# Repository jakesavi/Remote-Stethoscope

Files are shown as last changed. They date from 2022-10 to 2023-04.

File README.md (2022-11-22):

# Remote-Stethoscope

## Communication
https://discord.gg/RNJMYp4RQn

## Data Pipeline 
- Heart
- Microphone
  - filter input frequency range
    - what frequency ranges are of interest?
    - do we want a discrete or analog UI for controlling inputs on the stethoscope?
  - amplify signal if analog mic
  - convert to digital signal if not a digital mic
  - potentially explore using multiple types of microphones and use input concensus to further filter out noise
- microcontroller processes raw input into audio format
- microcontroller streams unencrypted data to PC as a microphone
- PC software encrypts audio stream and sends to doctor in real-time
  - PC software on doctor's end decrypts audio stream and broadcasts to system audio output
- PC software (on user end or doctor's end?) saves an encrypted copy of the recording as an audio file (and sends it to doctor if on user's end)
  - Advantages of user's end file save:
    - Potential for packet loss of done on doctor's end
  - Advantages of doctor's end file save:
    - Doctor can segment the incoming real-time stream based on when the patient switches which body part is being listened to, allowing for an easier time with labeling the saved data for potential data visualization and AI applications

## Getting Started
1. Connect the Xiao RP2040 to your computer via USB-C cable
    - In order to boot the microcontroller into flashable mode, hold down the microcontroller push button labeled "B" from before the connection to the computer happens until after the LED on the microcontroller turns on.
2. To flash a new microcontroller with the software to act as a microphone, copy the file usb_microphone.uf2 into the root directory of the microcontroller.  It should automatically disconnect after this and reboot into a device that the system will refer to as MicNode
3. Connect the Xiao RP2040 to the MEMS digital microphone.  See "./doc/BreadboardCircuit.png" for a demonstration of of how the circuit should appear.
    - The microcontroller and microphone boards should both be soldered to their respective pin headers in order for this to work.
4. Open Audacity, select Microphone (MicNode) as your recording device, begin recording, and confirm that the microphone is recording a clear signal.
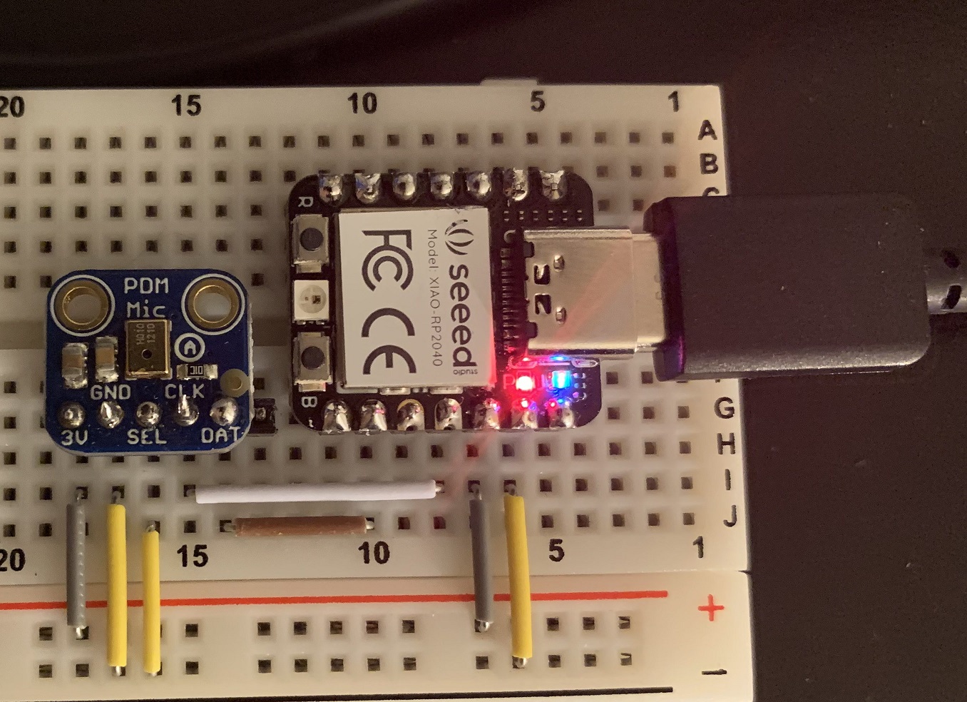
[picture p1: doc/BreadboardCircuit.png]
Circuit board connection map


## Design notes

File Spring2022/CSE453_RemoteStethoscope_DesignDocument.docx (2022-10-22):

# Design Document

# Remote Stethoscope

For use in Telemedicine

CSE 453 Hardware/Software Integrated System Design

Spring 2022

Andrew Burneson,

Yusuf Elazzazi,

Avi Tombak

# Table of Contents:

Project Background 3

Summary 3

Outcomes and Deliverables 3

Expected Timeline 3

Specifications 3

Requirements 3

Constraints 3

Design 3

Design Overview 3

Remote Stethoscope Block Diagram 4

Circuit Diagram 4

3D Printed Stethoscope Bell 5

Bill Of Materials 5

Prototyping 5

Testing/Verification 6

References Documentation 6

Project Delivery 6

# Project Background

Summary:

This project is a remote stethoscope device for use in telemedicine appointments. The remote stethoscope consists of a 3D printed stethoscope bell, a simple stethoscope diaphragm, a digital microphone, and a microcontroller. The remote stethoscope functions as a USB microphone device that can be used by patients during a telemedical appointment with a doctor. The remote stethoscope transmits audio of a patient’s heart, lung, and artery sounds for the doctor to listen to.

Client: Dr. Robert Gatewood

Outcomes/Deliverables: A Functional Prototype Remote Stethoscope

Expected Timeline: Delivered by end of the Spring 2022 semester

# Specifications

Requirements:

- The stethoscope will have a microphone to record audio input.
- The audio captured by the microphone will be amplified and converted to a digital signal.
- The digital audio will be transmitted to a computer using USB-C.
- The doctor will be able to receive the stethoscope audio over the internet.
- The stethoscope will come with a user manual for patients.

Constraints:

- The production cost of the stethoscope must be under $50.
- The microphone must record audio with a frequency between 20 and 2k Hz.
- The audio quality must be good enough for the doctor to diagnose the patient.

# Design

Design Overview:

The remote stethoscope was designed with simplicity and cost as its primary considerations. The stethoscope is to be used by patients directly, putting their health in their hands and allowing them to be more involved in their care. In its current design, the stethoscope acts very similarly to a traditional stethoscope. It must be pressed onto the chest to pick up a heartbeat or elsewhere for other bodily sounds. Instead of listening to the heartbeat via earpieces connected to the stethoscope, the remote stethoscope transmits audio of the heartbeat over USB C to a patient’s computing device. USB C was chosen as it is becoming widely used and available across multiple devices (PCs, smartphones, laptops, tablets). This model of the stethoscope consists of a 3D printed stethoscope bell, a plastic film diaphragm, a PDM MEMS microphone, and a microprocessor. The stethoscope has an overall production cost of $24.45.

Remote Stethoscope Block Diagram:

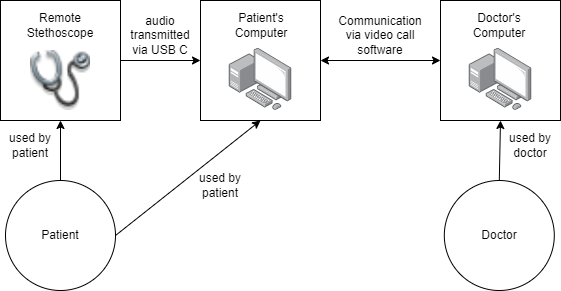
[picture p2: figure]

Circuit Diagram:

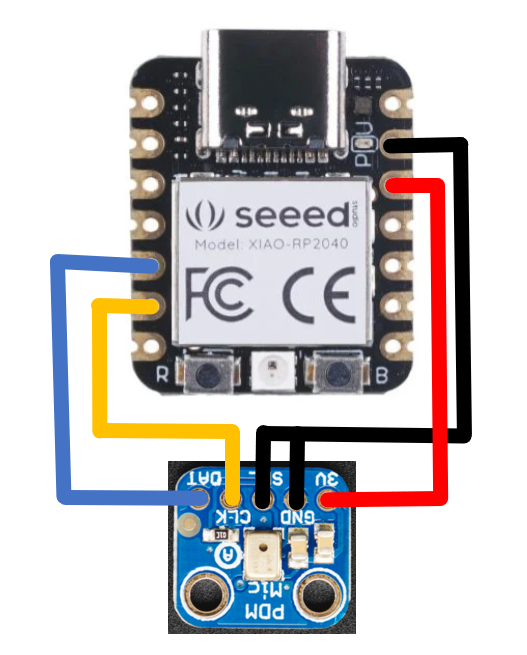
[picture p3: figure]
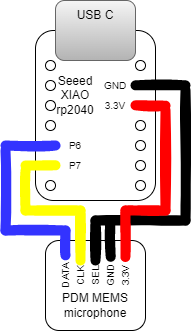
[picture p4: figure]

3D Printed Stethoscope Bell:

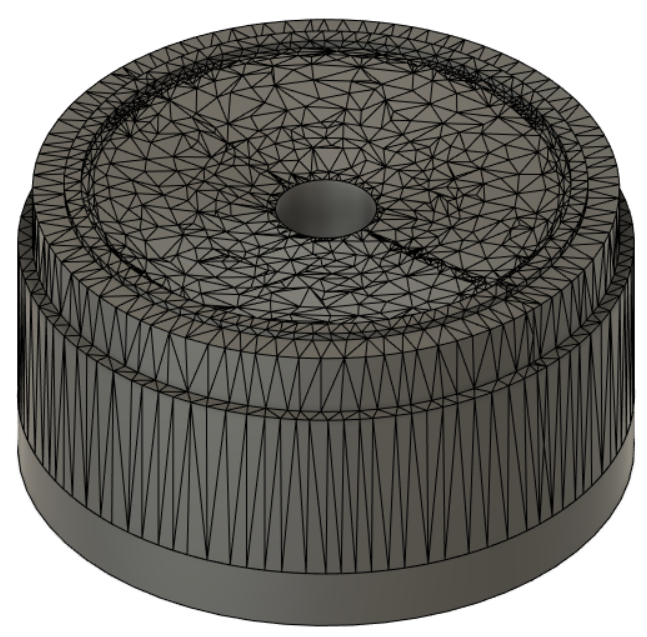
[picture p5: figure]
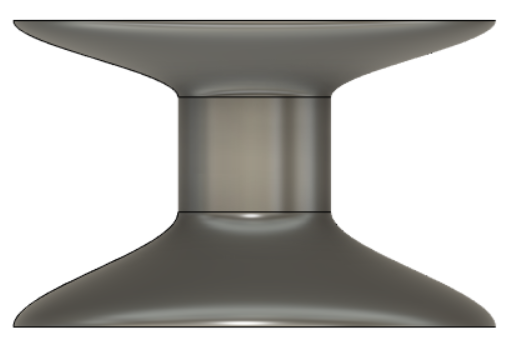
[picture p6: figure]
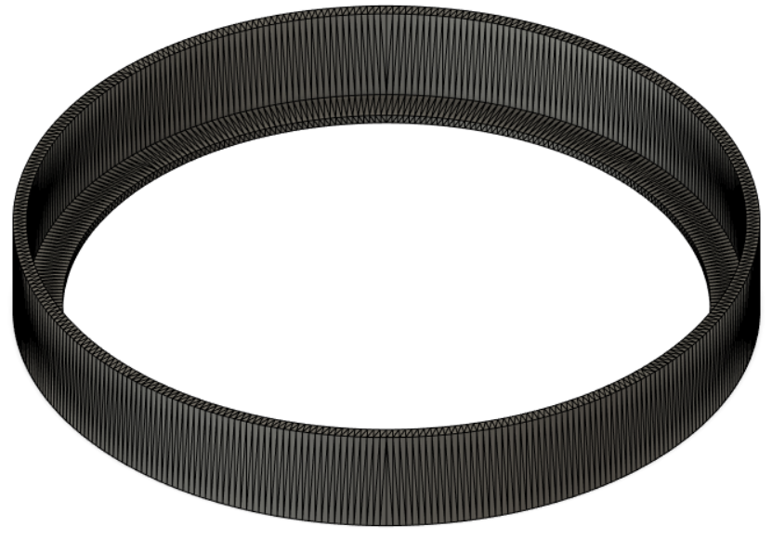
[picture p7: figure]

Stethoscope Head Stethoscope Handle Stethoscope Ring

Choice of Materials:

The following materials were chosen to ensure the stethoscope is well within the specified cost constraint.

- Seeed XIAO rp2040 Microcontroller for USB Microphone Device
- Adafruit PDM MEMS Microphone Breakout Board
- 3D Printed PLA Stethoscope Bell
- Report Cover Plastic Sheet for Stethoscope Diaphragm

Bill of Materials:

The bill of materials associated with this project is attached alongside this project and can also be found at: CSE453_RemoteStethoscope_BOM.docx (https://docs.google.com/document/d/1wtiuyCxSb0sfxCKr2Fo5E8p2Mzp0vhBN)

Prototyping:

This project has gone through many prototyping stages. There was an iterative design process for determining various factors of the design, including the stethoscope bell, the diaphragm, the microphone model, and the use of tubing. As this project was inherited from a previous group in this course, the prototyping first stated with testing and verification of their design. This involved circuit building and analysis. Moving on from the previous group’s work, a functional prototype utilizing a 3D printed stethoscope bell, and passing the audio recordings to a laptop via audio jack was created. This prototype does not reflect the final design but has sufficient audio quality for detecting heartbeats and other bodily sounds. After developing a working prototype with audiojack ( a far simpler protocol than usb audio) the next step was to develop the working USB microphone model. This was achieved using a Digital PDM MEMS Microphone and the Seeed XIAO rp2040 Microprocessor. The microprocessor was programmed using the ARM Developer Ecosystem Microphone Library for Pico. The stethoscope bell itself went through different iterations as well, first starting with an open source 3D printed stethoscope model found on thingiverse. A cone shaped stethoscope was also tested in prototyping. This design was modified to be larger and fit the stethoscope circuit. With this larger 3D printed stethoscope and microprocessor circuit, the final prototype design was produced.

Testing/Verification:

In order to test and verify the behavior of the stethoscope, audio recordings were taken from the USB device using the program Audacity. A heartbeat recording can be accessed here:

https://drive.google.com/file/d/168XsQzZ5z6yvc9MNJsx-UgUAekHpegst/view?usp=sharing

References Documentation:

The following references were used throughout the development of this project:

https://www.thingiverse.com/thing:2826304

https://github.com/ArmDeveloperEcosystem/microphone-library-for-pico

https://www.adafruit.com/product/3492?utm&gclid=CjwKCAjwyryUBhBSEiwAGN5OCKDwwzdIQs_0lFxj7LmzrSDqmjgVPmQrksxNdygoIFctDELNPU6doRoCHDYQAvD_BwE

https://www.seeedstudio.com/XIAO-RP2040-v1-0-p-5026.html?gclid=CjwKCAjwyryUBhBSEiwAGN5OCI7WuxWBaaORjbeqGIfqSfpMNfckhvS_kDpI4O9fUpDoT5V69NSQwBoCbkgQAvD_BwE

# Project Delivery

This Project will be ready for final delivery with a functional prototype, however our client is yet to schedule a date for delivery. The deliverables include our functional prototype remote stethoscope, and a user guide for patients.

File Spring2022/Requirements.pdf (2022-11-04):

# Remote Stethoscope Project Requirements Document

Prepared for: Dr. Robert Gatewood
Prepared by: Andrew Burneson, Yusuf Elazzazi, Avi Tombak, Quinn Tarbell

# Goals

The goal of this project is to develop an electronic stethoscope for use in remote medicine as well as an application to accompany it. To accomplish this, we will design, prototype, and test the stethoscope and program. The project will be completed by the first of April, 2022 with further refinement afterwards as necessary.

# Features

## Stethoscope

- Form Factor
- The stethoscope will have a head that attaches to a separate electronic component.
- The electronics will be inside a case small enough to fit in one hand.
- The stethoscope will have a cord that connects the electronics to a usb C port.
- The stethoscope head will have a microphone within it.
- The microphone will have a frequency range from 20 to 2k Hz.
- The microphone will have a high enough quality to be able to hear heart sounds.
- The electronics will include an amplification circuit.
- The electronics will include an analog to digital converter.

## Software

- The stethoscope will have one application designed to be used in conjunction with it.
- The application can create a host session.
- The user must input a password to start a host session.
- While hosting the user can accept requests to connect from other users.
- Once connected the host will receive audio from the other user’s application. ■ The host can listen to the received audio.
■ The host can adjust the volume of the received audio.
■ The host can record the received audio.
- The application can connect to a host application using a password.

- While connected to a host, the application can receive audio from the electronic stethoscope.
- While receiving audio the application will send the audio to the host application
- The application will function on Windows 10.

# Users

The stethoscope and application will be used by doctors and patients conducting remote medicine. The doctors include cardiologists, general practitioners, and etc. The patients include people who are quarantined, people who have trouble moving, the elderly, and people who live too far away from the doctor.
The doctor only needs to use the application. First the doctor will start the application and create a host session. Second, the doctor will send the patient the password and accept their request to connect. Then, the doctor will direct the patient to use the stethoscope and listen to the audio from it. The doctor can adjust the volume or record the audio using the application. The patient uses both the stethoscope and the application. First the patient will start the application and connect the stethoscope to the computer. Then they will input the password given by the doctor into the application. The patient will use the stethoscope to listen to their body as directed by the doctor.

# Constraints and Dependencies

- The stethoscope must cost less than fifty dollars.
- The stethoscope and application must be HIPPA compliant.
- The user must have a computer.
- The computer must run Windows 10.
- The computer must have a usb C port.
- The computer must have an internet connection.
- The user must have a connection to the internet.
- The internet connection must be fast enough to transmit real time audio.
- The doctor and patient must have a method to communicate with each other.

Description:
A remote stethoscope is to be designed for use in telemedicine appointments.
The patient will receive the stethoscope alongside a kit with a user guide and all necessary components.
The stethoscope will be used by the patient directly with doctor guidance via a video call. There is also a software component that will allow the doctor to analyze the stethoscope readings remotely.

The following is a diagram of the process the remote stethoscope recording will undergo from patient to doctor.

Remote Stethoscope Specifications:
- A cost of less than $50
- Sufficient audio quality and frequency range for hearing sounds of body systems (heart, lungs, gi)
- Record the audio and transmit it between the patient and doctor via other computing devices (i.e. a personal computer and/or a smartphone)
- Sufficient audio amplification and volume control
- Sufficient background noise filtration to isolate the body system sounds

Remote Stethoscope Patient/User Kit:
- Includes the remote stethoscope
- Includes any necessary cables and connectors for the stethoscope to interface with computers
- Includes a user guide document which has instructions on how to use the stethoscope

Remote Stethoscope Software Interface:
- Allow for easy analysis of the stethoscope readings by the doctor
Goals:
The aim of this project is to continue the work done by the previous group in charge of the remote stethoscope project. The goal is to create a cheap electronic stethoscope as well as a system to transmit audio over the internet for use in telemedicine. The stethoscope must be cheap in order for it to be accessible to patients.

Users:

The remote stethoscope would be used by patients and doctors conducting telemedicine. The patients will be within their homes. The patients will run the application and connect the stethoscope to their computer with a cable. The doctor will also run the application and connect it to the patient’s application over the internet. The patient will then place the stethoscope on their body under the doctor's direction while the doctor listens to the audio using the application on their own computer.

Features:
The stethoscope will be able to detect sounds in the range of frequencies necessary for diagnosis. It will amplify the audio and have sufficient audio quality in order for the doctor to diagnose medical issues. The stethoscope will connect to a computer through a cable. The application will record the audio from the stethoscope and transmit it over the internet to the doctor’s computer. The application on the doctor’s computer will play the audio and allow them to control the volume.

Constraints:
The stethoscope must cost less than 50 dollars.

Requirements:
The patient and doctor must both have a computer and an internet connection.

# Outline

I. Goals
A. Develop Remote Stethoscope
1. Design
2. Prototype
3. Test
B. Develop Software
1. Design
2. Prototype
3. Test
C. Complete by Deadline (add deadline) II. Features
A. Remote Stethoscope
1. Form Factor
a) Has a stethoscope head
b) Has an electronic circuit
c) Head connects to circuit
d) Circuit in case small enough to fit in hand
2. Connector between circuit and computer (choose one connector)
3. Microphone in stethoscope head
a) (add frequency range)
b) High sound quality (not specific)
4. Amplification Circuit
a) Amplification factor (undecided)
b) Analog to Digital Converter (ADC)
(1) May be part of computer if using microphone jack
B. Software
1. Can create a host
a) Generates password
b) Can accept requests to connect from guests
c) Receives audio from guest
(1) Plays received audio
(2) Can adjust volume
(3) Can record audio
2. Guest
a) Can request to connect with a host using a password
b) Receives audio from stethoscope
c) Sends audio from stethoscope to host
3. Functions on OS (choose one operating system)
III. Users
A. Who uses it?
1. Doctors
a) Cardiologists

b) General Practitioners
c) (Ask Dr. Gatewood for more)
2. Patients
a) Quarantined
b) Trouble moving
c) Elderly
d) Live to far away
B. How is it used
1. Doctors
a) Launch application
b) Start hosting
c) Give patient password
d) Accept patient’s connection request
e) Instruct patient to use stethoscope
f) Listen to audio from stethoscope
g) Adjust volume
h) Record audio
2. Patient
a) Launch application
b) Connect stethoscope to computer
c) Input password given by doctor
d) Use stethoscope as directed by doctor IV. Constraints
A. Must cost less than $50
B. Must be HIPPA compliant
V. Dependencies
A. User must have a computer
1. The computer must have the correct OS
2. The computer must have the correct connection
3. The computer must be able to connect to the internet
B. The user must have an internet connection
1. The connection must be fast enough to transmit real time audio
C. The doctor and patient must be able to communicate

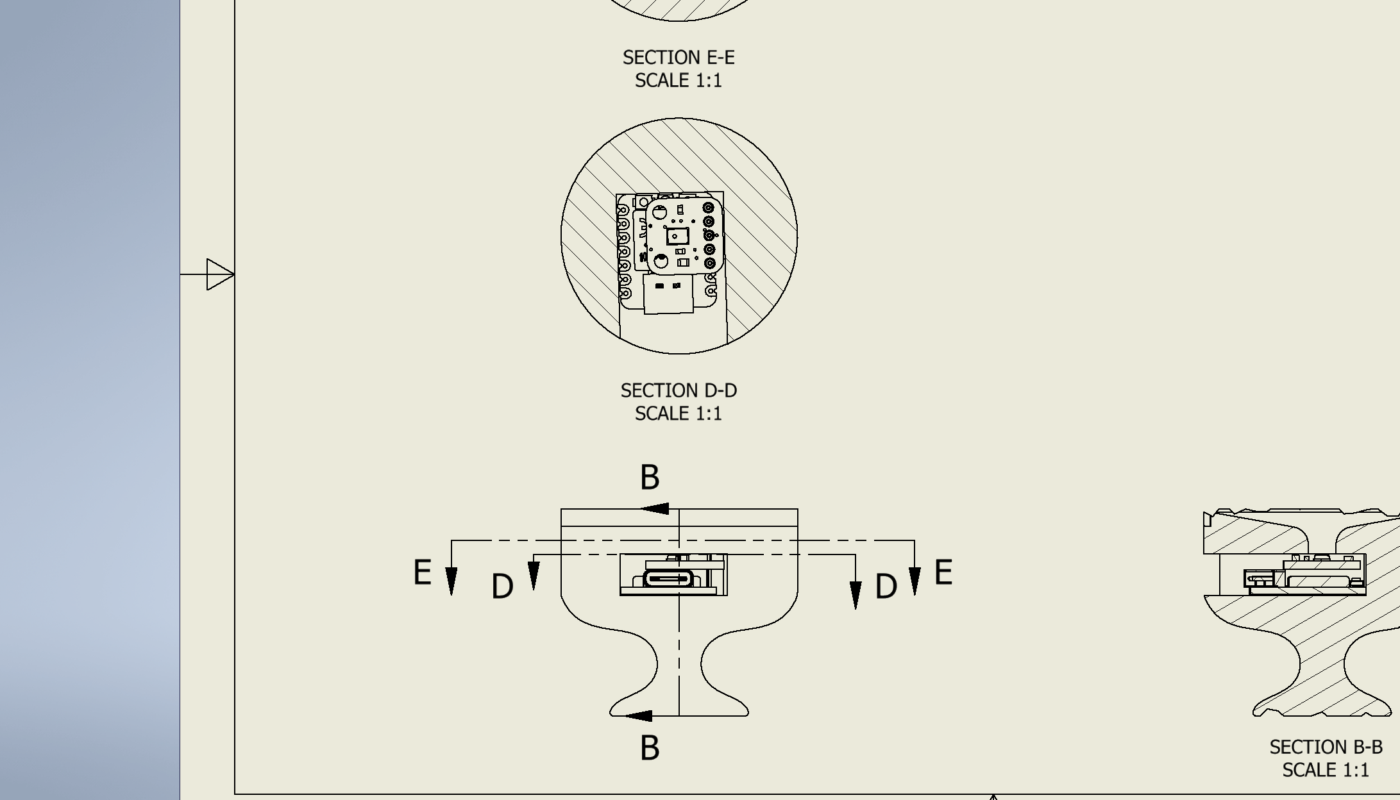
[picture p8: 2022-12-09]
3D_models/Fall2022_revision/Full_Stethoscope_Body.png

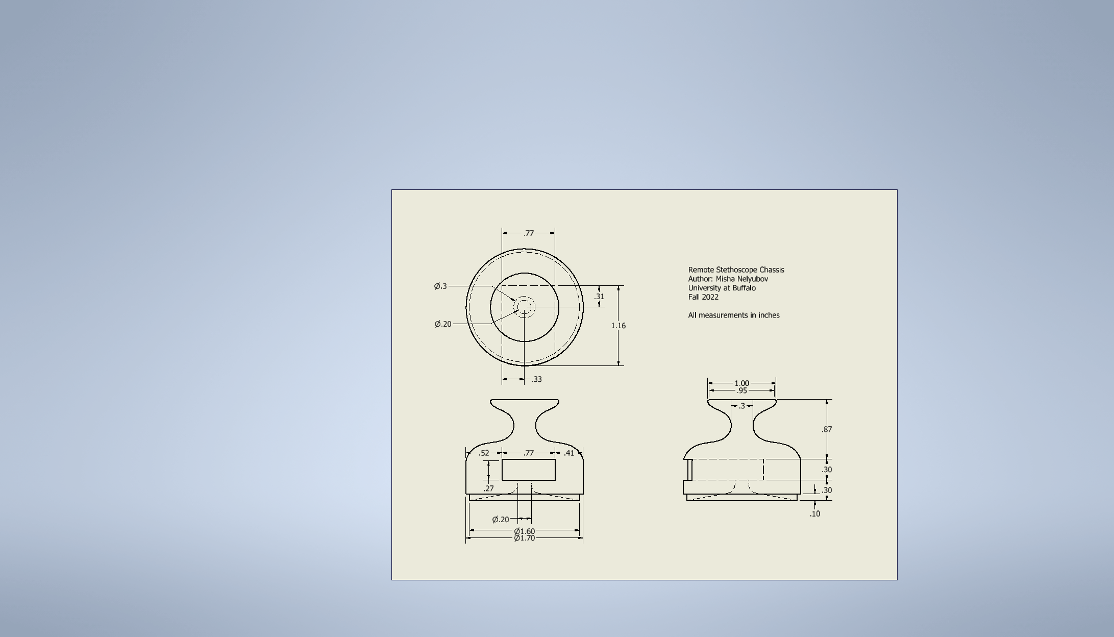
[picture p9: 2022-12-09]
3D_models/Fall2022_revision/Stacked_Case.png

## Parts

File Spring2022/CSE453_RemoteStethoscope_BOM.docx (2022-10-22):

Image | Part Name & Part Number | Supplier / Manufacturer | Part Type & Use | Quantity | Cost per Purchase | Cost per Stethoscope | Link | Associated Documentation

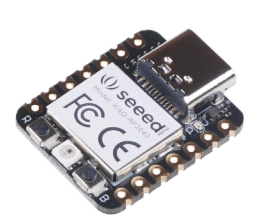
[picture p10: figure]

| XIAO rp2040 SKU: 102010428 | Seeed | Microcontroller for powering stethoscope and allowing it to be treated as a USB microphone | 1 board | $5.40 | $5.40 | seeed_XIAO_rp2040 (https://www.seeedstudio.com/XIAO-RP2040-v1-0-p-5026.html) | datasheet (https://files.seeedstudio.com/wiki/XIAO-RP2040/res/rp2040_datasheet.pdf)

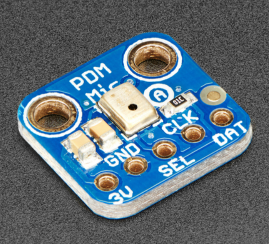
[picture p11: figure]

| PDM MEMS Microphone Breakout PRODUCT ID: 3492 | Adafruit | Microphone for stethoscope functionality | 1 board | $4.95 | $4.95 | PDM_MEMS_mic (https://www.adafruit.com/product/3492?utm) | mic_documentation (https://cdn-learn.adafruit.com/downloads/pdf/adafruit-pdm-microphone-breakout.pdf)

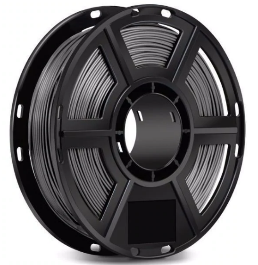
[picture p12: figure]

| PLA Filament for Finder, Dreamer, Inventor Series, & Adventurer 3 Part Number: N/A | FlashForge | 3D Printer Filament for stethoscope material | head: 130.7g handle: 63.87g ring: 7.47g total: 202.4g | $34 | ~ $13.76 | PLA_filament (https://flashforge-usa.com/collections/materials/products/pla-filament-for-finder-dreamer-and-inventor-models) | N/A

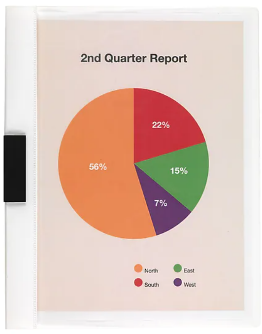
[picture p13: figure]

| Slide Locking Report Covers, Letter, White, 5/Pack Item #: 919872 Model #: 20592 | Staples | Plastic Sheet for stethoscope diapragm | 1 cutout (4 per sheet) | $6.79 | ~ $0.34 | diaphragm_material (https://www.staples.com/Staples-Side-Lock-Report-Covers-5-Pack-White-20592/product_919872) | N/A
| | | | | | Total cost: ~ $24.45

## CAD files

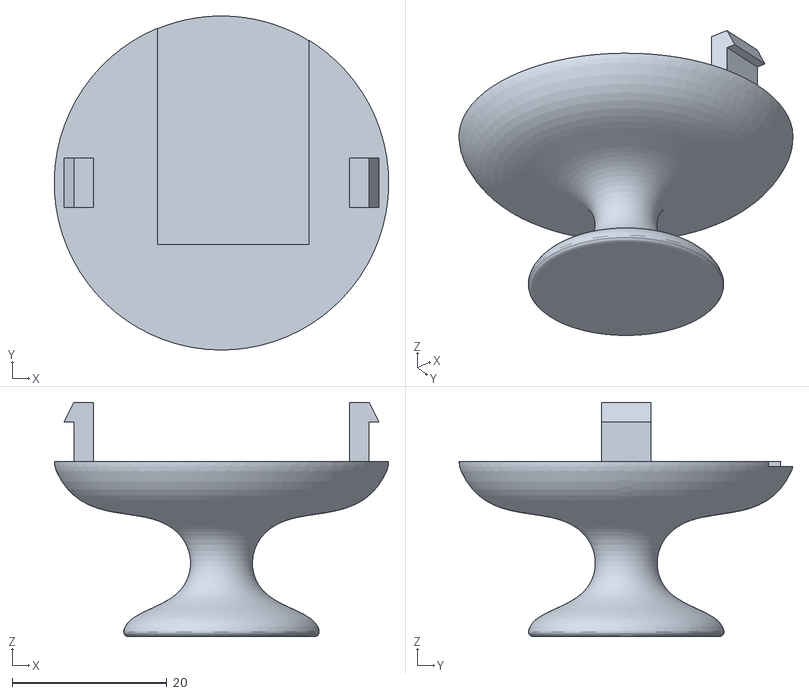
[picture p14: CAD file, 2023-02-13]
3D_models/Fall2022_revision/Stacked_Case_handle.stl
43.2 x 43.1 x 30.3

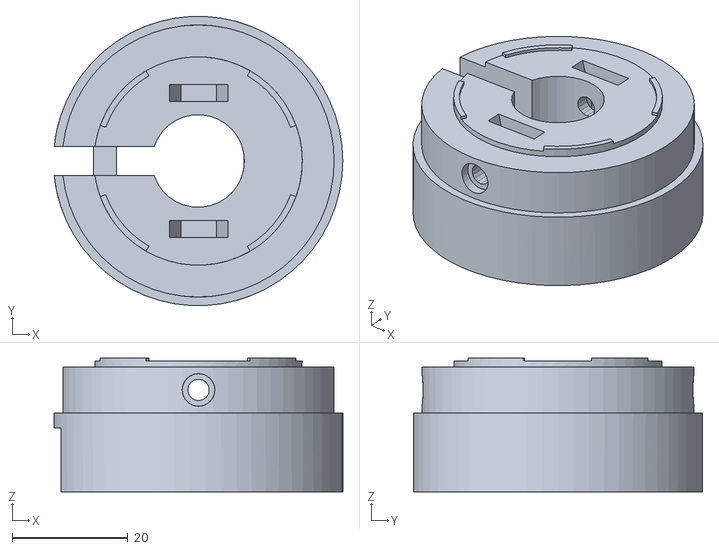
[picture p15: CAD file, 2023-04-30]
3D_models/ThonkLabs 1ne/STL files/PiezoMount.stl
49.9 x 49.9 x 23.1

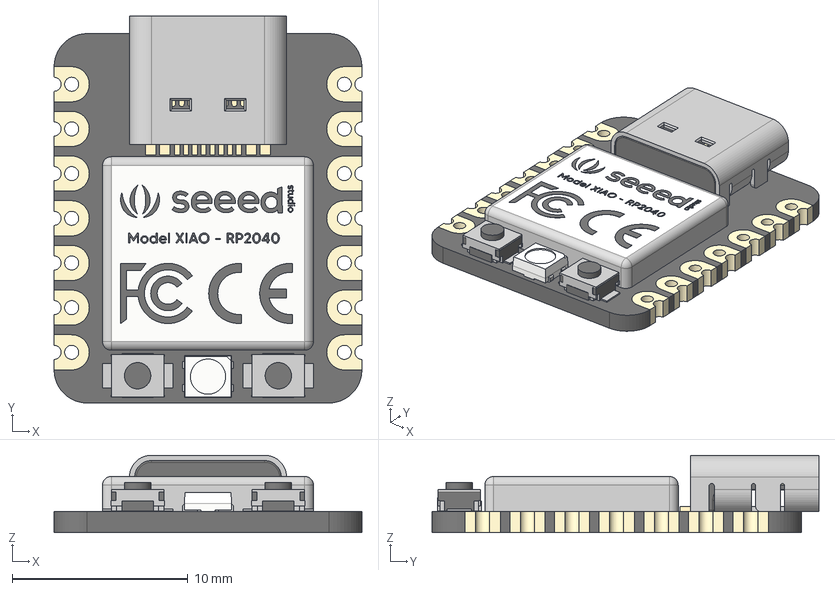
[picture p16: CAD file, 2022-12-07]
3D_models/xiao_rp2040/Seeed Studio XIAO RP2040 v26.step
17.5 x 22.0 x 4.40 mm
type-c v2
smd_button v3
DOUT
DIN
VSS
VDD
smd_button v3(Mirror)

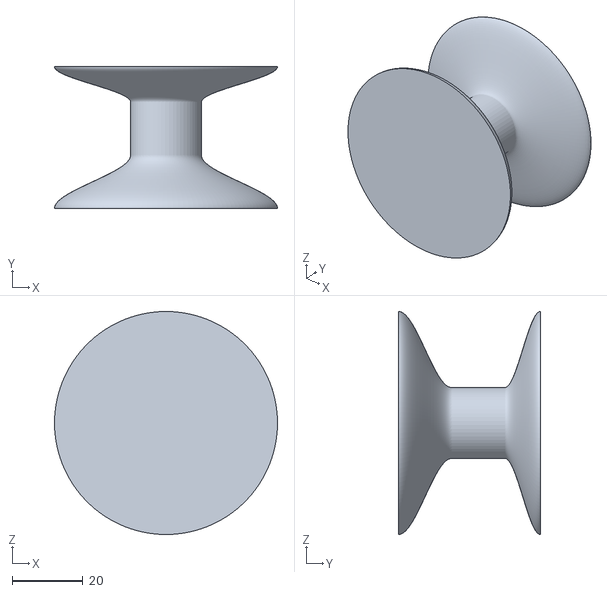
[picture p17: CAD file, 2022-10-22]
Spring2022/CSE453_RemoteStethoscope_3DPrints/handle.stl
63.0 x 40.0 x 63.0

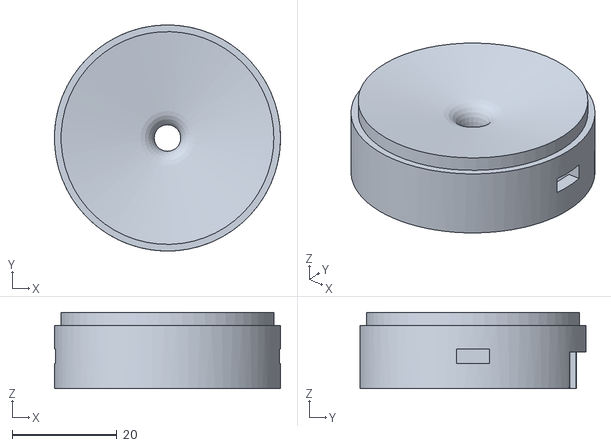
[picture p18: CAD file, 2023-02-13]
3D_models/Fall2022_revision/Stacked_Case_container.stl
43.2 x 43.2 x 14.6

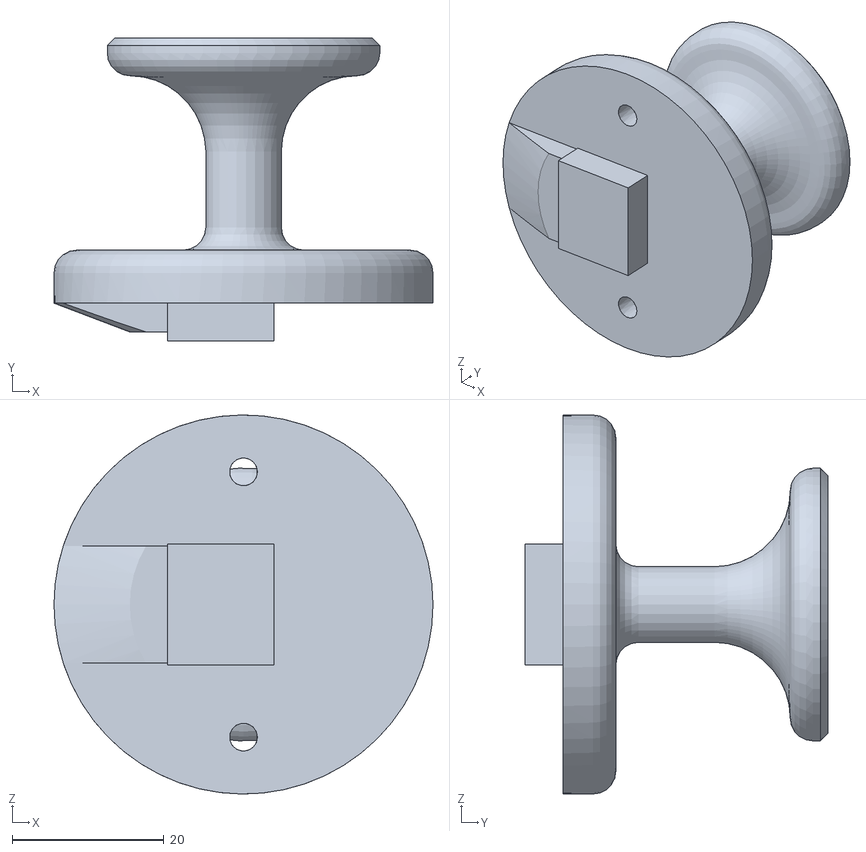
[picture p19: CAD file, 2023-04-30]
3D_models/ThonkLabs 1ne/STL files/holding_socket.stl
50.0 x 40.0 x 50.0

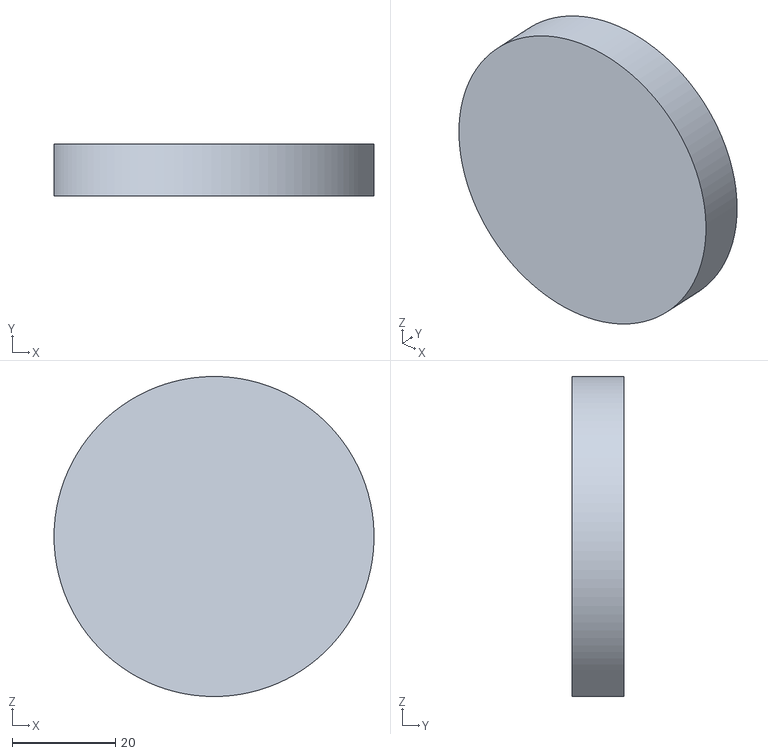
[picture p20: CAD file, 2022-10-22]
Spring2022/CSE453_RemoteStethoscope_3DPrints/diaphragm_stencil.stl
62.0 x 10.0 x 62.0

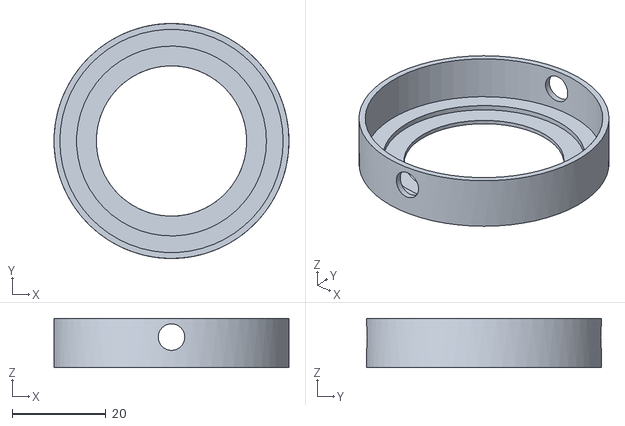
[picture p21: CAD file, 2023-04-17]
3D_models/ThonkLabs 1ne/STL files/Diaphragm_lock.stl
50.0 x 50.0 x 10.5

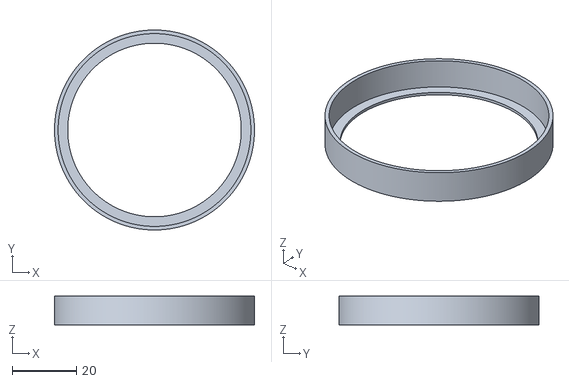
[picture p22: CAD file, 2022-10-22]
Spring2022/CSE453_RemoteStethoscope_3DPrints/ring.stl
62.2 x 62.2 x 9.00

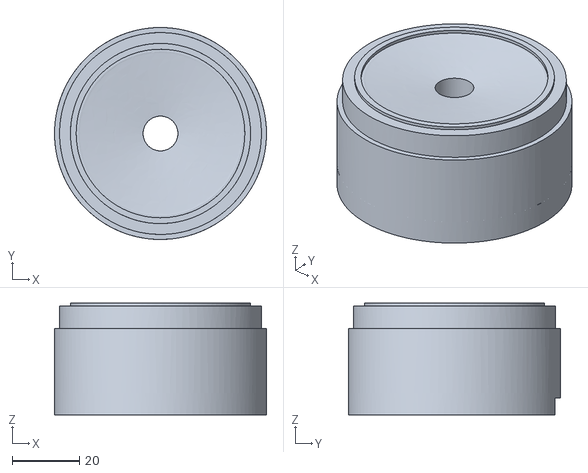
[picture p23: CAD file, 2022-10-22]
Spring2022/CSE453_RemoteStethoscope_3DPrints/head.stl
63.0 x 63.0 x 33.2

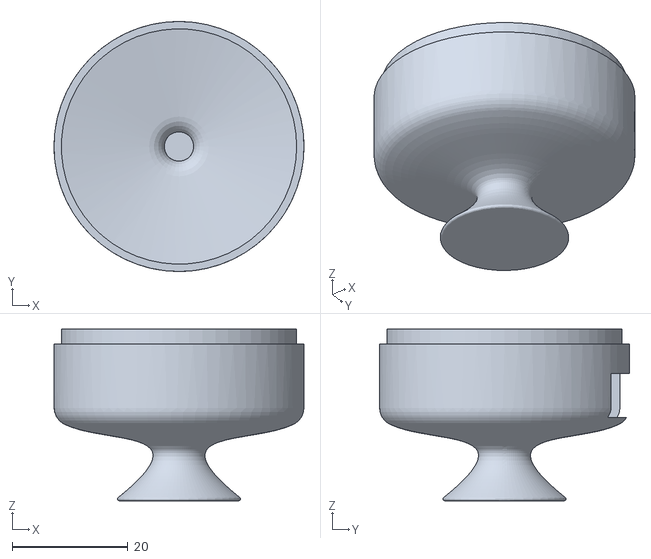
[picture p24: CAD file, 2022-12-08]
3D_models/Fall2022_revision/Stacked_Case.stl
43.2 x 43.2 x 29.6

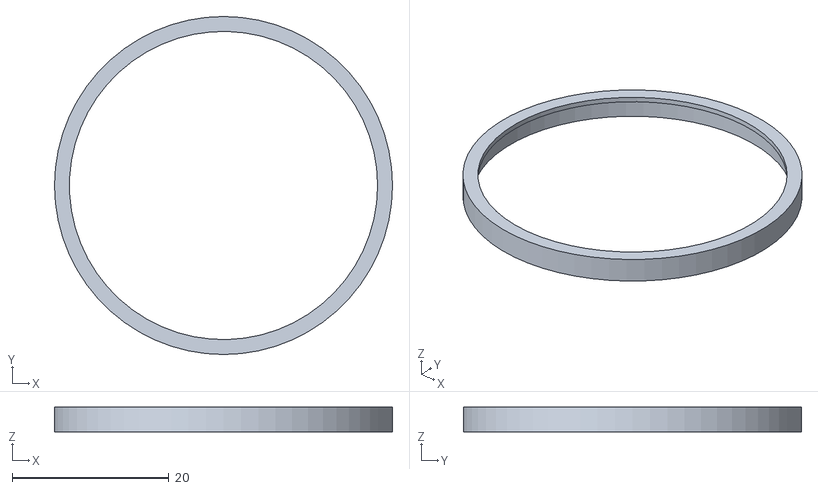
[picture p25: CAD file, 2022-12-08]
3D_models/Fall2022_revision/Diaphragm_Ring.stl
43.2 x 43.2 x 3.17

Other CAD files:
3D_models/Fall2022_revision/Full_Stethoscope_Body_2_part_case.dwg
3D_models/Fall2022_revision/Full_Stethoscope_Body.dwg
3D_models/ThonkLabs 1ne/SeparateDiaphragm/PiezoMount.dwg
3D_models/ThonkLabs 1ne/SeparateDiaphragm/holding_socket.dwg
3D_models/ThonkLabs 1ne/SeparateDiaphragm/Diaphragm_lock.dwg
3D_models/ThonkLabs 1ne/SeparateDiaphragm/Diaphragm.dwg
3D_models/Diaphragm_Film.ipt
3D_models/Diaphragm_Ring.ipt
3D_models/Fall2022_revision/Full_Stethoscope_Body.iam
3D_models/Fall2022_revision/Full_Stethoscope_Body_2_part_case.iam
3D_models/Fall2022_revision/IC_pin.ipt
3D_models/Fall2022_revision/OldVersions/IC_pin.0004.ipt
3D_models/Fall2022_revision/Stacked_Case.dwg
3D_models/Fall2022_revision/Stacked_Case.ipt
3D_models/Fall2022_revision/Stacked_Case_container.dwg
3D_models/Fall2022_revision/Stacked_Case_container.ipt
3D_models/Fall2022_revision/Stacked_Case_handle.dwg
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

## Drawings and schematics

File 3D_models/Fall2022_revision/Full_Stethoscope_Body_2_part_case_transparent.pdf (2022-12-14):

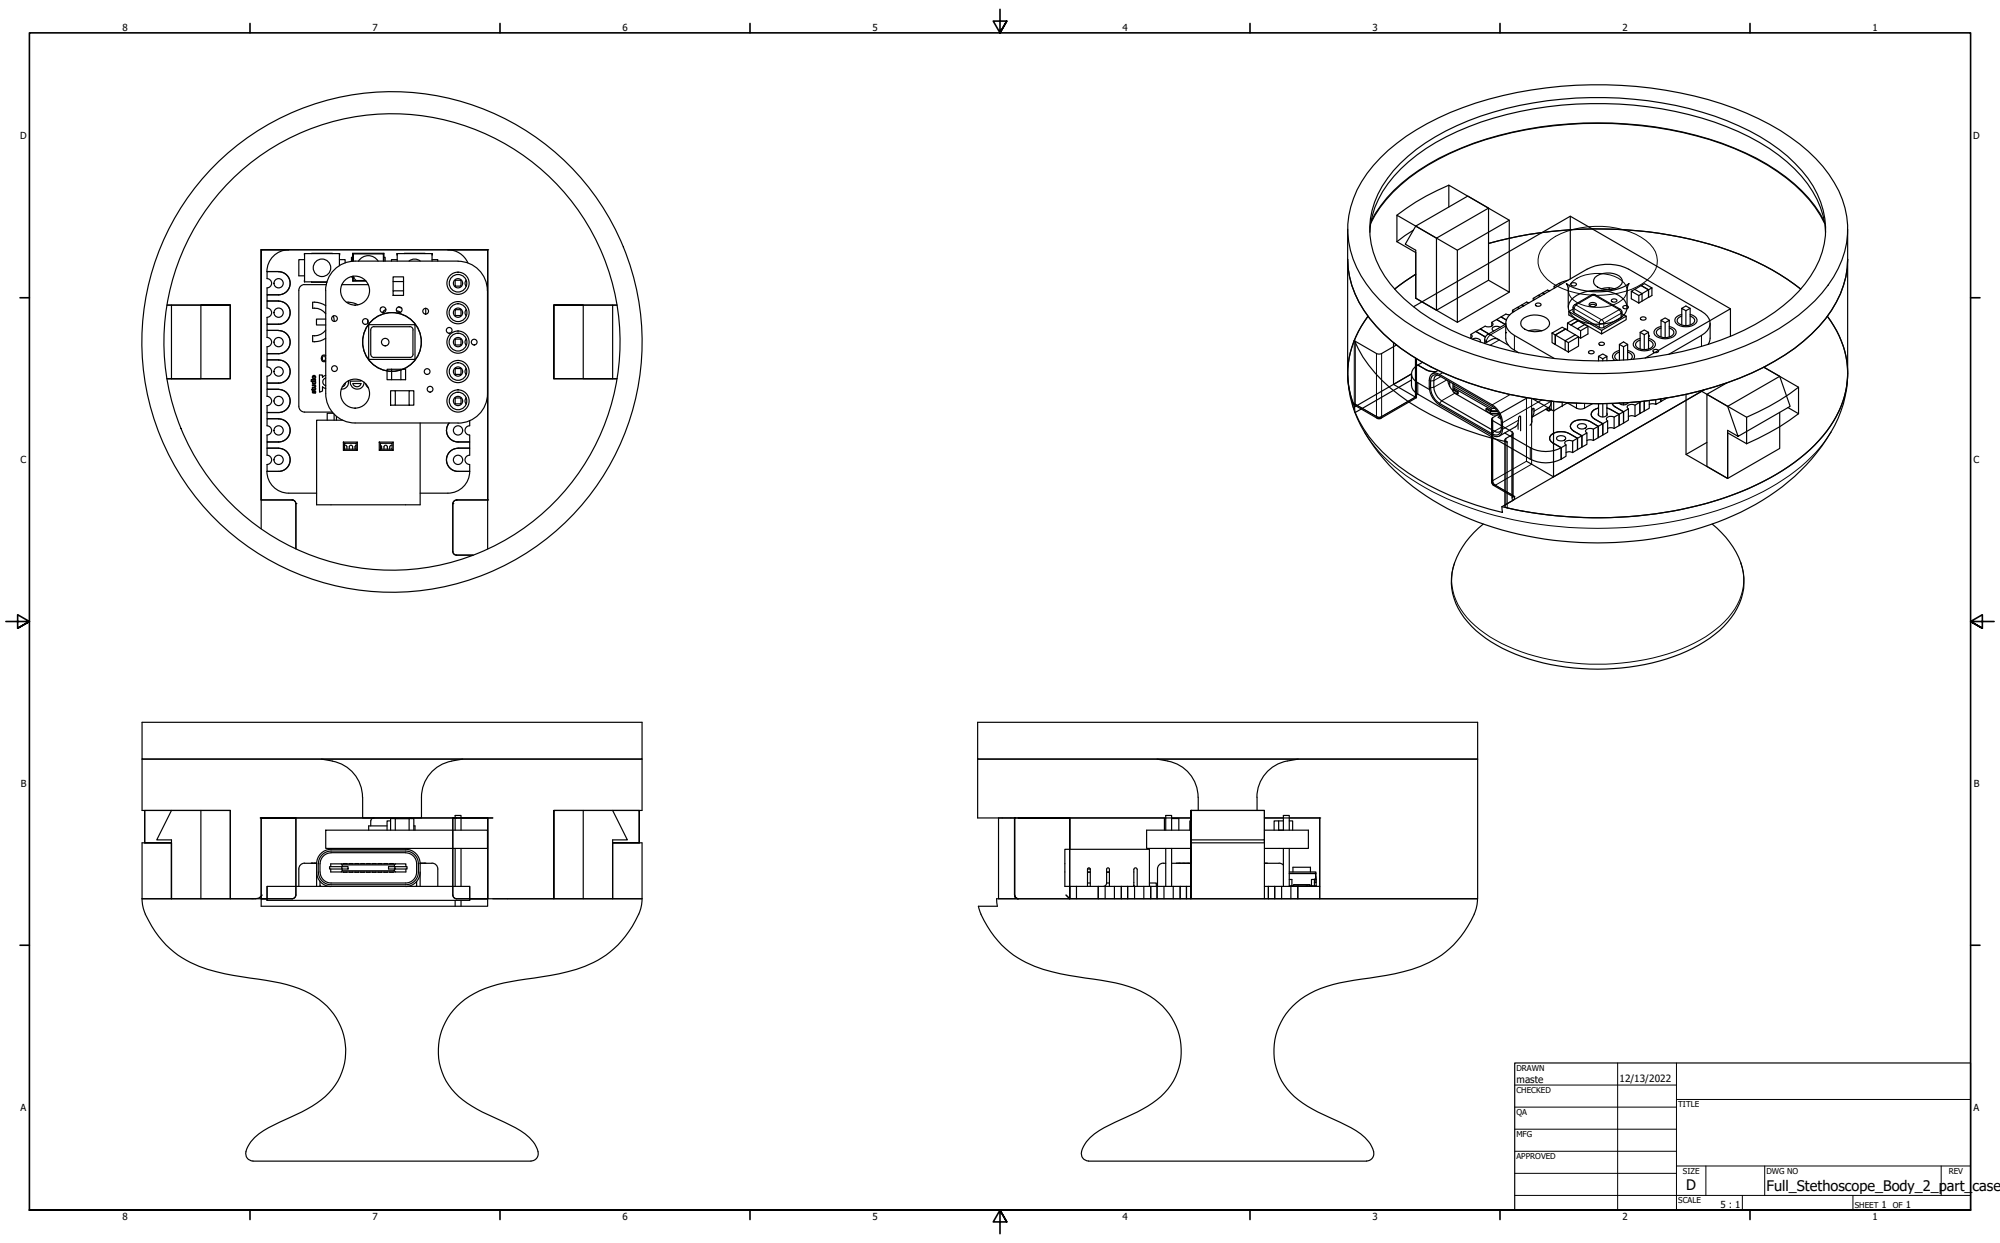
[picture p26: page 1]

DRAWN maste | 12/13/2022

CHECKED

MFG

APPROVED

SIZE D | DWG NO | REV

SCALE 5 : 1 | | SHEET 1 OF 1

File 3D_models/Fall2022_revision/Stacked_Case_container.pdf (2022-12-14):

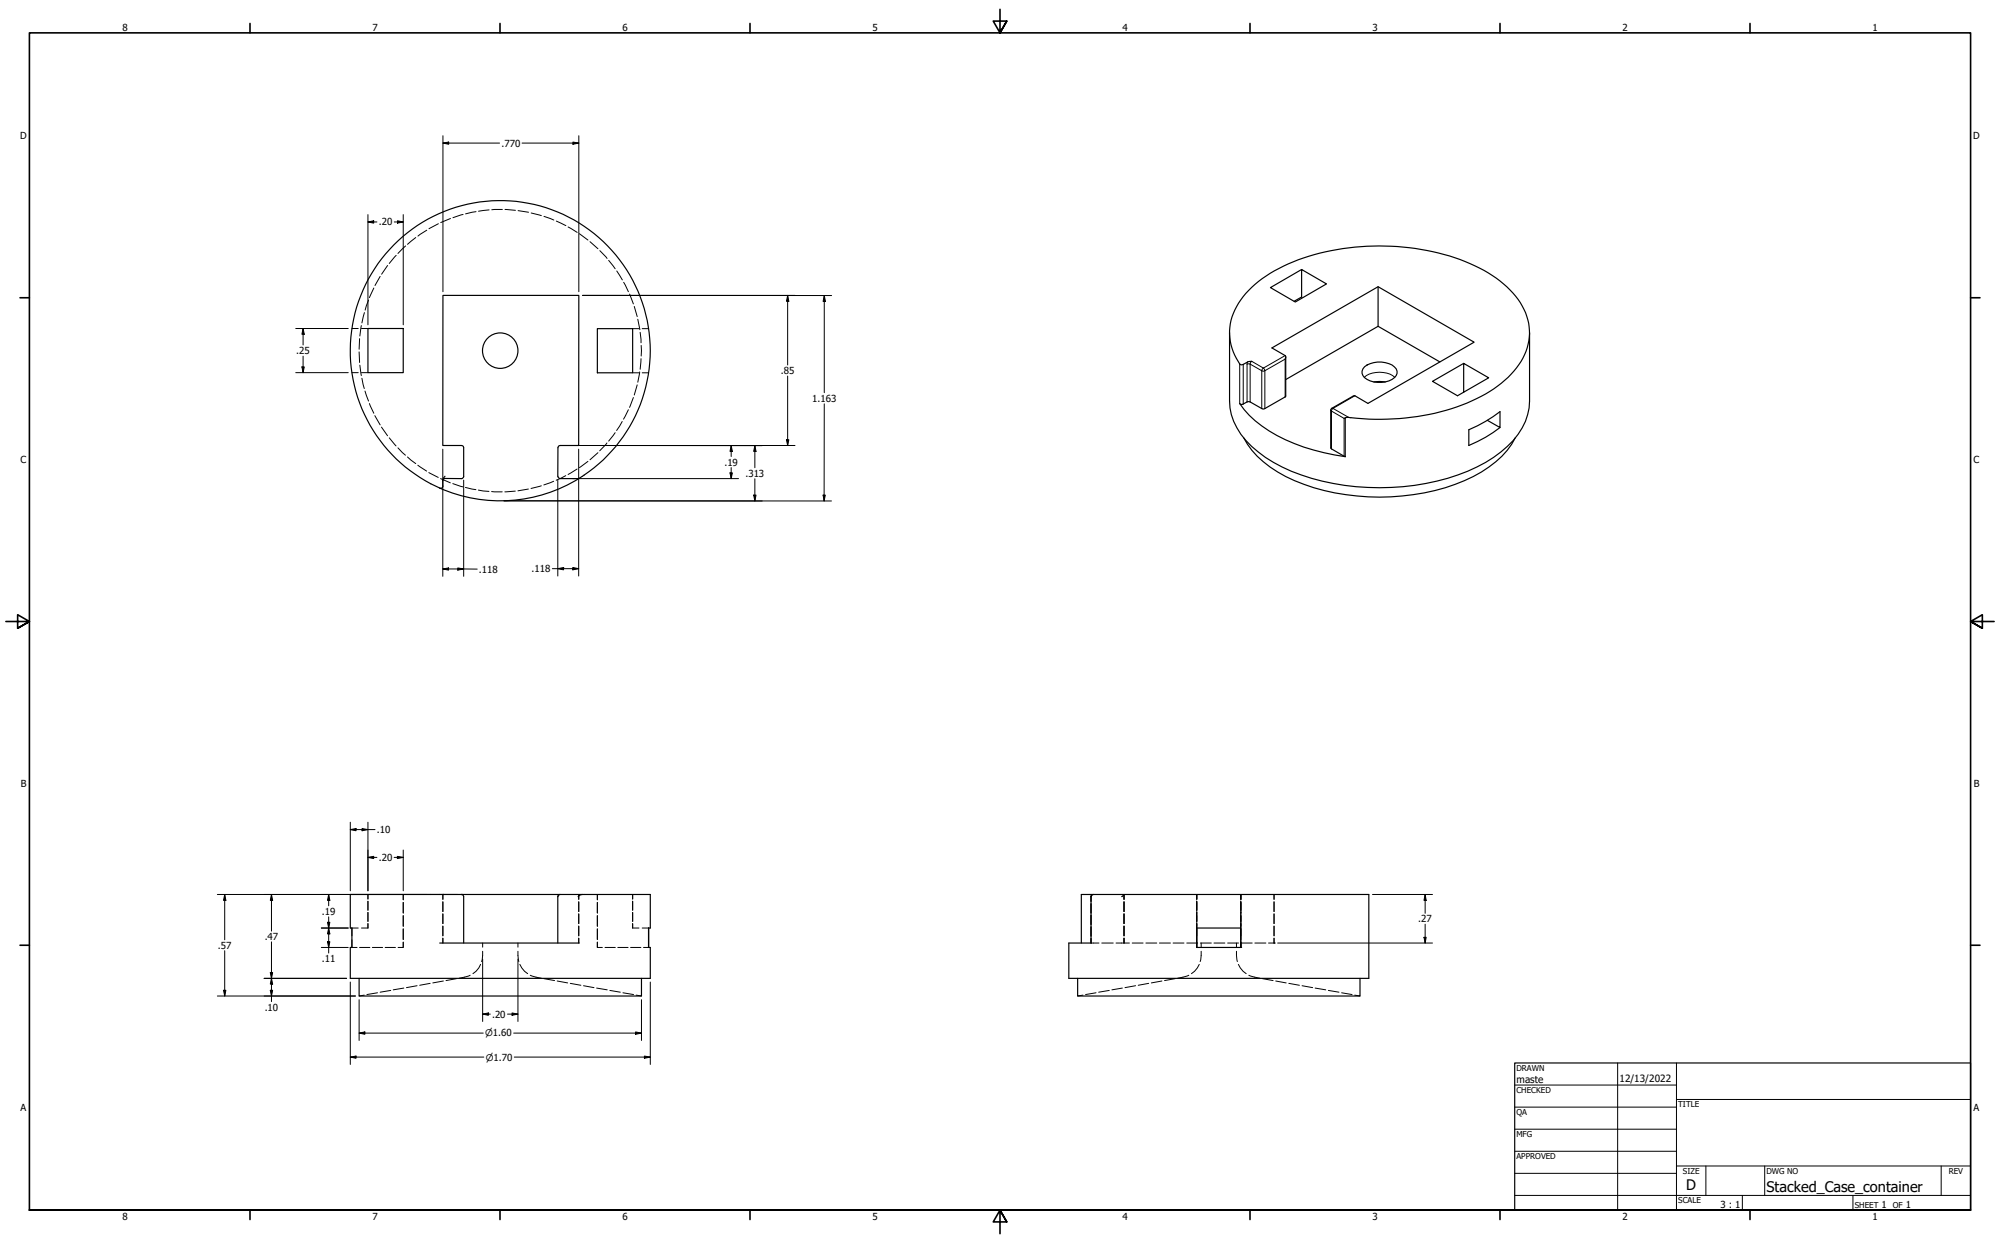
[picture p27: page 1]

DRAWN maste | 12/13/2022

CHECKED

MFG

APPROVED

SIZE D | DWG NO Stacked_Case_container | REV

SCALE 3 : 1 | | SHEET 1 OF 1

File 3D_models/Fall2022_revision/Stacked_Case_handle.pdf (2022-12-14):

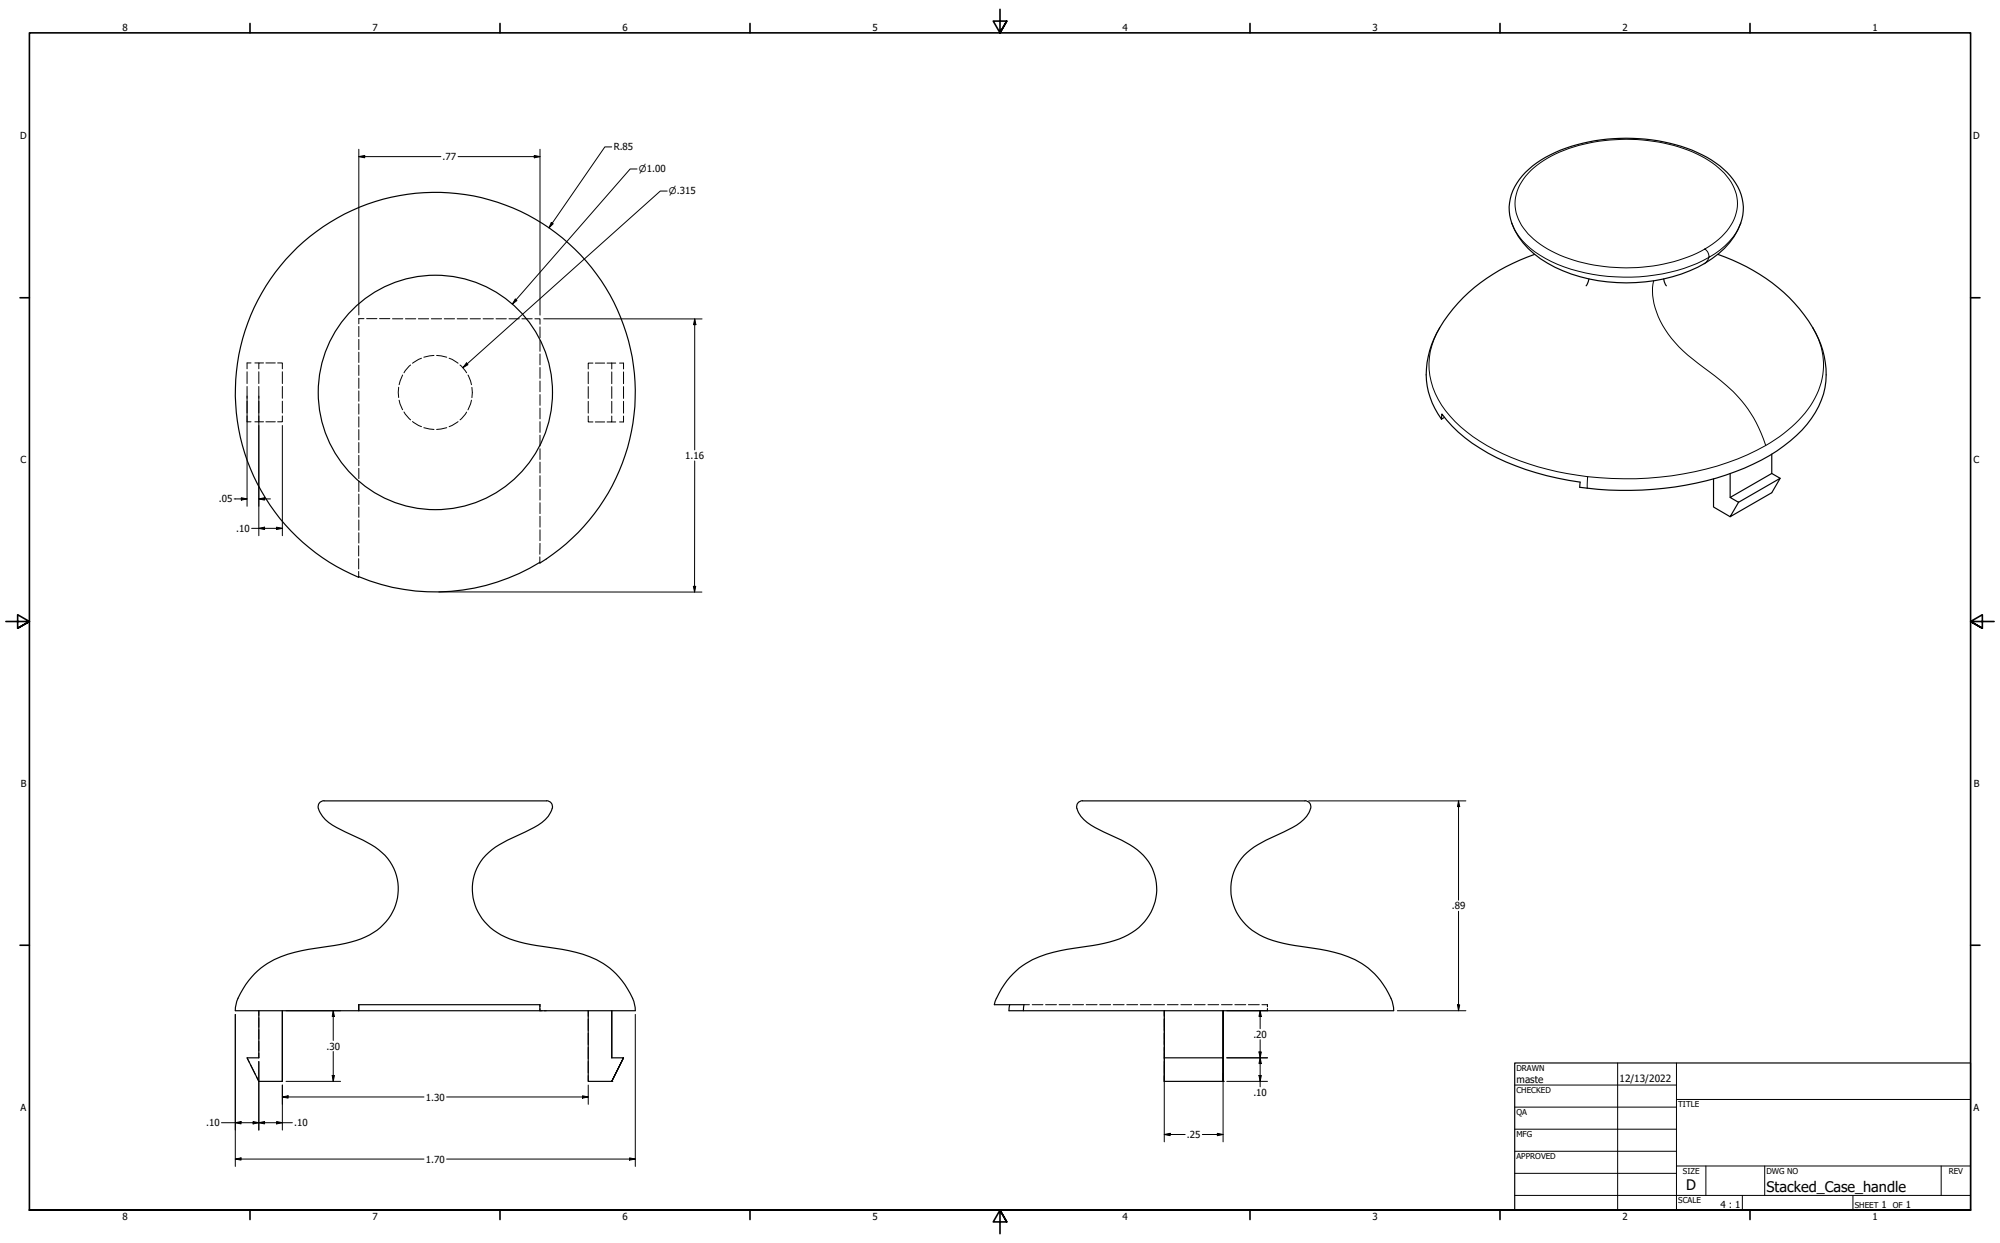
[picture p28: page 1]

DRAWN maste | 12/13/2022

CHECKED

MFG

APPROVED

SIZE D | DWG NO Stacked_Case_handle | REV

SCALE 4 : 1 | | SHEET 1 OF 1

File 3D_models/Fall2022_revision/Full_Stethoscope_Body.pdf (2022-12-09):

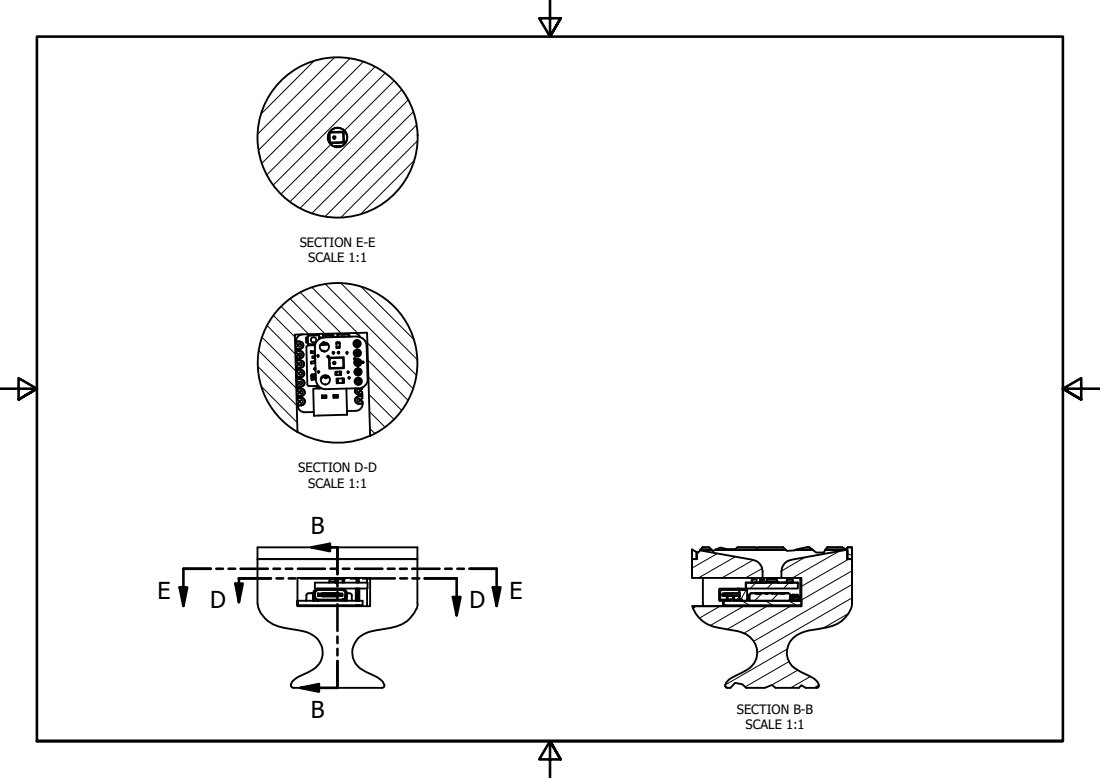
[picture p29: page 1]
SECTION B-B SCALE 1:1; SECTION D-D SCALE 1:1; SECTION E-E SCALE 1:1

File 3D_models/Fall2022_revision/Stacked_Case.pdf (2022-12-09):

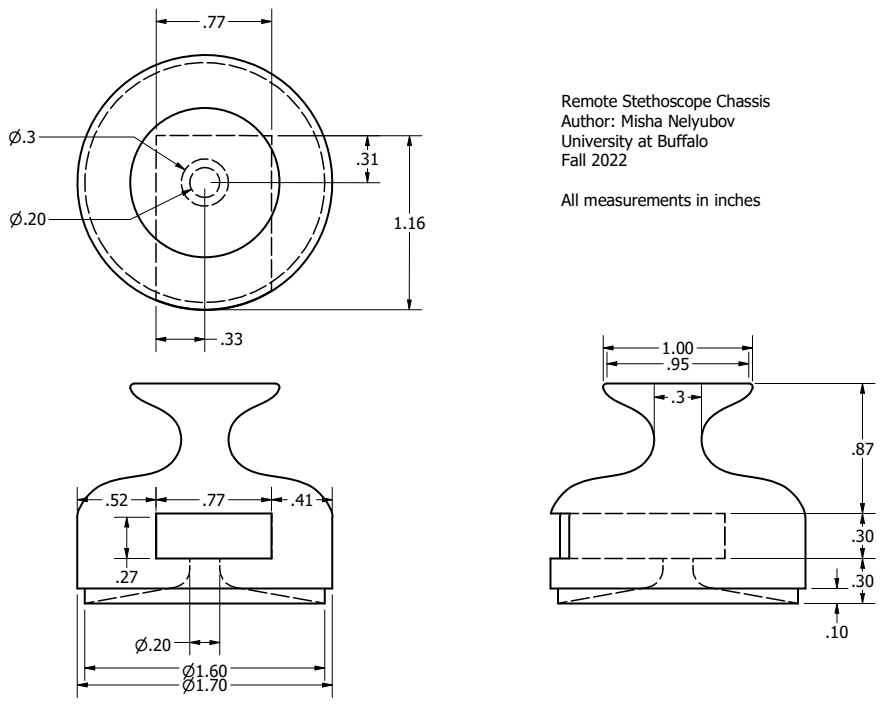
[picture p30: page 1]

Remote Stethoscope Chassis
Author: Misha Nelyubov
University at Buffalo
Fall 2022

All measurements in inches

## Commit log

2022-10-01 Created rough draft of pipeline
    Looking for feedback and refinement on what we want to do at each stage of the process.
2022-10-22 Imported files from Spring 2022
    Thanks to Avi for sending the files
    [diaphragm_stencil v3.f3d, diaphragm_stencil.stl, handle v3.f3d, handle.stl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]
2022-10-28 Renamed archive file
    removed old file names
    [diaphragm_stencil v3.f3d, diaphragm_stencil.stl, handle v3.f3d, handle.stl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]
2022-11-22 Created an effective circuit
    This system requires both the microcontroller and microphone to be soldered to the set of pins that they came with in order to operate properly
2022-11-22 Created instructions to replicate current headway
2022-11-22 Added image of circuit to readme
2022-12-02 Create breadboard to solder board mapping.xcf
2022-12-02 Create breadboard to solder board mapping.png
2022-12-07 Imported 3D models for mic and upc
    [0603-NO.ipt, 0805-NO.ipt, Board.ipt, DIN.ipt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]
2022-12-08 created old versions (?)
    automatically done by inventor
    [Full_Stethoscope_Body.0004.iam, IC_pin.0002.ipt, Stacked_Case.0004.ipt]
2022-12-09 Created design drawings to go with designs
    [Board.0002.ipt, Board.ipt, Full_Stethoscope_Body.0001.dwg, Full_Stethoscope_Body.0004.iam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]
2022-12-10 aligned pins, todo split chassis
    aligned pins, TODO: split chassis into 2 halves w/ Cantilever Snaps-fits
    [Full_Stethoscope_Body.0007.iam, Full_Stethoscope_Body.0010.iam, Full_Stethoscope_Body.iam, PCB Component.0001.iam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]
2022-12-14 Created 2-part chassis, todo: connection latch
    [Full_Stethoscope_Body_2_part_case.iam, Stacked_Case_container.0002.ipt, Stacked_Case_container.ipt, Stacked_Case_handle.0002.ipt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]
2022-12-14 created drawings for case parts
    [Full_Stethoscope_Body_2_part_case.0002.iam, Full_Stethoscope_Body_2_part_case.dwg, Full_Stethoscope_Body_2_part_case.iam, Stacked_Case_container.0002.dwg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]
2022-12-14 exported .DWG files to .PDF
    created PDF files of drawings for adoption into presentation as desired
    [Full_Stethoscope_Body_2_part_case.0002.dwg, Full_Stethoscope_Body_2_part_case.0002.iam, Full_Stethoscope_Body_2_part_case.0003.iam, Full_Stethoscope_Body_2_par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]
2022-12-15 created STL files for 3D prints
    [Stacked_Case_container.stl, Stacked_Case_handle.stl]
2022-12-15 Created stacked case handle+container print file
2023-02-13 Create FFT.ipynb
    Create FFT-checkpoint.ipynb
    explaining process
    attempting various filters
2023-02-28 Created 3D model based on the ThinkLabs One
    [Diaphragm.0002.ipt, Diaphragm.ipt, Diaphragm_Ring.stl, Diaphragm_lock.ipt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]
2023-02-28 Created STL files for components that can be printed
    [Diaphragm.stl, Diaphragm_lock.stl, PiezoMount.stl, holding_socket.stl]
2023-03-02 radius, wire access, support height buffs
    Buffed diaphragm support height, increased piezo wire hole size, increased radius for diaphragm
    [Diaphragm_lock.0001.ipt, Diaphragm_lock.ipt, Inner_Components.0001.iam, Inner_Components.0002.iam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]
2023-03-02 longer grip to improve ease of holding
    [holding_socket.0001.ipt, holding_socket.ipt]
2023-03-02 re-rendered STL files with new changes
    [Diaphragm_lock.stl, PiezoMount.stl, holding_socket.stl]
2023-03-02 Created second version of GCODE for printing
2023-03-06 version 3 - tighter tolerances, added 2mm through drill hole for connection
    [Diaphragm_lock.ipt, Diaphragm_lock.stl, Inner_Components.iam, PiezoMount.ipt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]
2023-03-11 WIP - don't print this commit
    [Diaphragm_lock.0005.ipt, Diaphragm_lock.0006.ipt, Diaphragm_lock.ipt, PiezoMount.0008.ipt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]
2023-03-15 versions 5,6
    [Diaphragm.ipt, Diaphragm_lock.0013.ipt, Diaphragm_lock.ipt, Diaphragm_lock.stl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]
2023-03-26 version 7 - now we're thinking with screws
    [Inner_Components.0007.iam, Inner_Components.0010.iam, Inner_Components.iam, PiezoMount.0016.ipt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]
2023-03-27 Version 8: increased space for nuts
    [Diaphragm.stl, PiezoMount.0020.ipt, PiezoMount.0022.ipt, PiezoMount.ipt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]
2023-04-12 V9, v10
    [Diaphragm_lock.0013.ipt, Diaphragm_lock.0019.ipt, Diaphragm_lock.ipt, Diaphragm_lock.stl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]
2023-04-17 Version 11 - back to the PDM
    [CircuitCell.0001.iam, CircuitCell.iam, Diaphragm_lock.0007.ipt, Diaphragm_lock.0019.ipt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]
2023-04-23 Version 12 - tightened PDM space, nut+bolt config space
    [CircuitCell.0001.iam, CircuitCell.0005.iam, CircuitCell.iam, IC_pin.0004.ipt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]
